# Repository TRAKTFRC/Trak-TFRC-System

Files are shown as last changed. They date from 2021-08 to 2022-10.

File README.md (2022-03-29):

# Trak-TFRC Product Feature Brief

## Primary goals

To develop and create low power and wireless open source technology that aids in large-scale and long-term wildlife research, conservation, and monitoring the health of ecosystems.
Device list:
1. Lora Base Station
2. TamaCollar
3. SmallCollar
4. MediumCollar
5. Mouse Motel
6. Tamarin Group Monitor  
Names subject to change  

### Device Feature List 

#### LoRa Base Station (AKA LoraTester1) 

A compact, portable device that can transmit and receive Lora messages, as well as store, display, and repeat them.  
- Durable IP66 enclosure with tamper-proof controls and secure mount points  
- LoRa 915Mhz/433Mhz with external SMA antenna mount  
- OLED display  
- SD card for data logging  
- RTC for accurate time keeping  
- GPS module  
- Rechargeable battery for operating in portable mode or when deployed in the field with solar power  
- Multiple modes of operation for receiving & logging LoRa messages, acting as a repeater, or transmitting data.  
- Optional features currently under consideration-  
    - USB connection to allow streaming of LoRa data in realtime to a PC  
    - Operating in a mesh network to extend the range of LoRa Message reception.  

Product usage & lifecycle notes- 
The LT1 units are primarily intended to be either used in handheld mode, or deployed as receivers  near feeding/monitoring sites to receive signals from collars. Ideally they should operate in a mesh to allow us to receive signals over a broader area in the dense amazonian jungle. 
As these are stationary devices mounted either to towers or tall vantage points, maintenance is much easier to perform and we hope these devices can last upwards of 5 years. 
The LT1 is a fairly flexible device, beyond changing it’s operating mode, users may wish to add additional sensors to monitor meteorological data or other.
 
#### TamaCollar

A lightweight tracker collar specifically designed to aid in tracking mature Tamarin species in the Peruvian Amazon.

- IP67 case/resin potting  
- Size- <30*25*6mm  
- Weight- <15g including ball chain collar  
- LoRa 915Mhz/433Mhz  
- RTC for accurate time keeping  
- GPS module  
- Primary non-rechargeable battery  
- User configurable transmission schedule  
- Optional features currently under consideration-  
    - Data logging in case of successful device retrieval

Product usage & lifecycle notes-  
The TC1 units are primarily designed to track wild Emperor Tamarins and Saddleback Tamarins, which are small new world monkeys weighing in at around 500g when grown.  
These lightweight disposable collars are shipped with a magnet taped near the internal reedswitch, and will activate when the vet who’s attaching the devices removes the magnet.   
In most cases, we will be programming the collars and shipping them sealed and ready-to-use, but configurable schedules are preferred. After a period of time, the crimp on the ball chain that holds the collar on will give way and fall off the animal. It is not expected to be recovered in most cases, but in the event that it is recovered, we can take apart the case and reuse the collars with minimal effort.  
Changes to make-  
- We are expecting to add a GPS antenna if required to help improve the GPS lock, both antennas would need to be as low-profile as possible. 
  
#### Tamarin Group Monitor

A deployable station to automate data collection from Tamarins and similar species
- Versatile and reconfigurable for different usecases
- Collects Weight, RFID readings, & images 
- flexible wake triggers
- Transmits data & trigger notifications over LoRa network.

#### SmallCollar

A minute tracker designed to aid in tracking smaller marsupials and rodents under 250g in the Peruvian Amazon.
At present, we are defining the brief for SC1 to allow us to monitor smaller animals than TC1, although no development has taken place yet. The goalposts are flexible so that we can push GPS monitoring to its absolute limits and bring the size and weight down as far as feasible. 
- IP67 case/resin potting  
- Size- TBD  
- Weight- <TBD including ball chain collar  
- LoRa 915Mhz/433Mhz  
- RTC for accurate time keeping  
- GPS module  
- Primary non-rechargeable battery  
- User configurable transmission schedule

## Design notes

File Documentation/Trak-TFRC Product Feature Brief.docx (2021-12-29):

# Trak-TFRC Product Feature Brief

# Primary goals

To develop and create low power and wireless open source technology that aids in large-scale and long-term wildlife research, conservation, and monitoring the health of ecosystems.

Device list:

1. Lora Base Station
2. TamaCollar
3. SmallCollar
4. MediumCollar
5. Mouse Motel
6. Tamarin Group Monitor

Names subject to change

# Device Feature List

## LoRa Base Station (AKA LoraTester1)

A compact, portable device that can transmit and receive Lora messages, as well as store, display, and repeat them.

- Durable IP66 enclosure with tamper-proof controls and secure mount points
- LoRa 915Mhz/433Mhz with external SMA antenna mount
- OLED display
- SD card for data logging
- RTC for accurate time keeping
- GPS module
- Rechargeable battery for operating in portable mode or when deployed in the field with solar power
- Multiple modes of operation for receiving & logging LoRa messages, acting as a repeater, or transmitting data.
- Optional features currently under consideration-
  - USB connection to allow streaming of LoRa data in realtime to a PC
  - Operating in a mesh network to extend the range of LoRa Message reception.

Product usage & lifecycle notes-

The LT1 units are primarily intended to be either used in handheld mode, or deployed as receivers near feeding/monitoring sites to receive signals from collars. Ideally they should operate in a mesh to allow us to receive signals over a broader area in the dense amazonian jungle.

As these are stationary devices mounted either to towers or tall vantage points, maintenance is much easier to perform and we hope these devices can last upwards of 5 years.

The LT1 is a fairly flexible device, beyond changing it’s operating mode, users may wish to add additional sensors to monitor meteorological data or other.

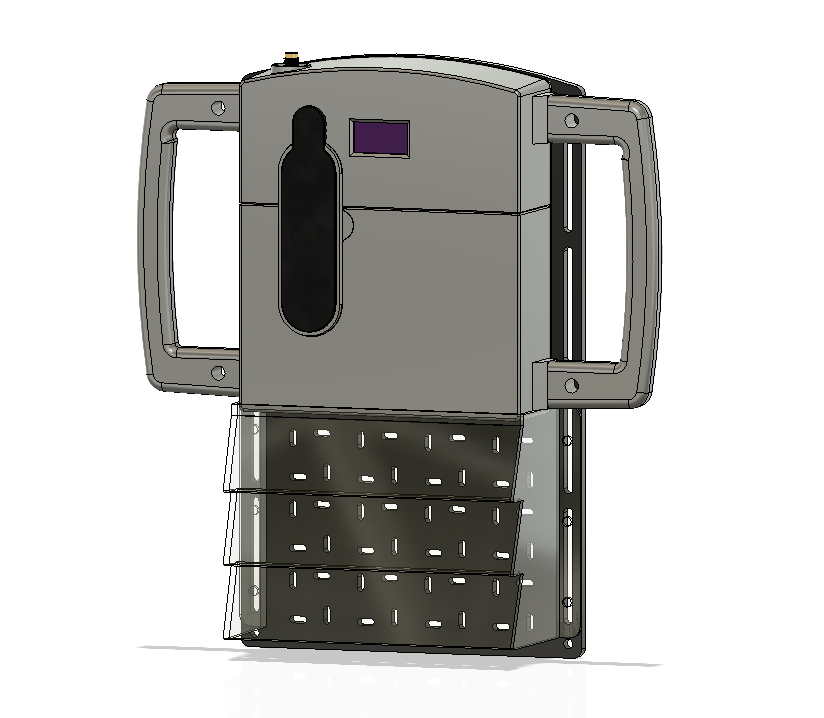
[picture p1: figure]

## TamaCollar

A lightweight tracker collar specifically designed to aid in tracking mature Tamarin species in the Peruvian Amazon.

- IP67 case/resin potting
- Size- <30X25X6mm
- Weight- <15g including ball chain collar
- LoRa 915Mhz/433Mhz
- RTC for accurate time keeping
- GPS module
- Primary non-rechargeable battery
- User configurable transmission schedule
- Optional features currently under consideration-
  - Data logging in case of successful device retrieval

Product usage & lifecycle notes-

The TC1 units are primarily designed to track wild Emperor Tamarins and Saddleback Tamarins, which are small new world monkeys weighing in at around 500g when grown.

These lightweight disposable collars are shipped with a magnet taped near the internal reedswitch, and will activate when the vet who’s attaching the devices removes the magnet.

In most cases, we will be programming the collars and shipping them sealed and ready-to-use, but configurable schedules are preferred. After a period of time, the crimp on the ball chain that holds the collar on will give way and fall off the animal. It is not expected to be recovered in most cases, but in the event that it is recovered, we can take apart the case and reuse the collars with minimal effort.

Changes to make-

- We are expecting to add a GPS antenna if required to help improve the GPS lock, both antennas would need to be as low-profile as possible.

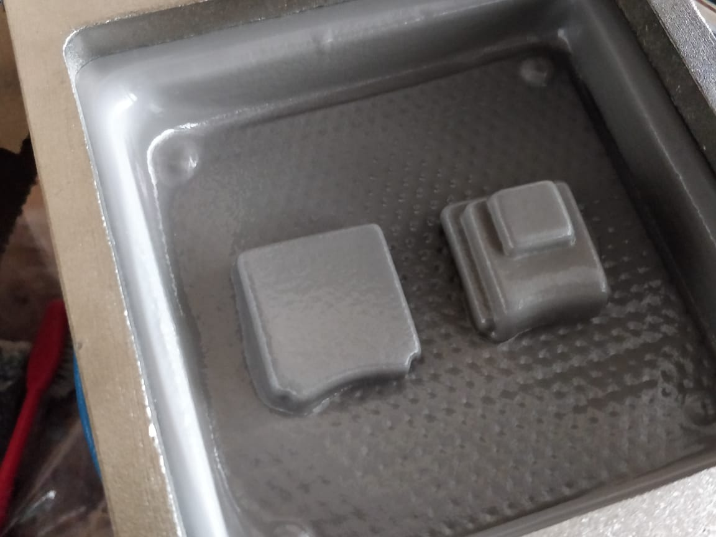
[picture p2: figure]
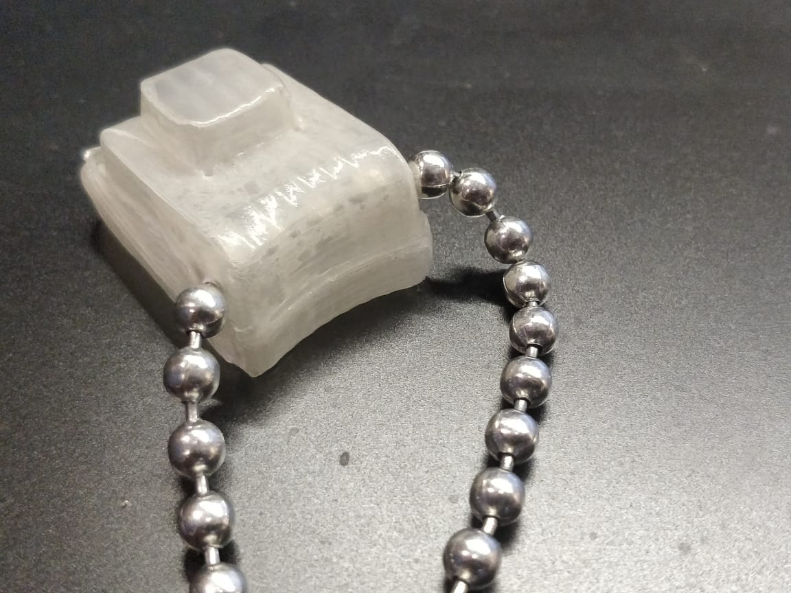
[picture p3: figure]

## SmallCollar

A minute tracker designed to aid in tracking smaller marsupials and rodents under 250g in the Peruvian Amazon.

At present, we are defining the brief for SC1 to allow us to monitor smaller animals than TC1, although no development has taken place yet. The goalposts are flexible so that we can push GPS monitoring to its absolute limits and bring the size and weight down as far as feasible.

- IP67 case/resin potting
- Size- TBD
- Weight- <TBD including ball chain collar
- LoRa 915Mhz/433Mhz
- RTC for accurate time keeping
- GPS module
- Primary non-rechargeable battery
- User configurable transmission schedule

## Tamarin Group Monitor-

A sample and data collection station to automate data collection from Tamarins and similar species.

- Autonomously collects data and transmits state via LoRa
- Stores and logs information to be manually retrieved via SD card
- Vital Data points-
  - Images
  - Weight
  - Subcutaneous RFID tag reading
  - Time
- Vital Sample points-
  - Hair/Fur
  - Faeces
  - Urine

Common points between TGM and Mouse Motel-

- Structure- Monitor unit
- Hardware- LoRa, Camera module, RTC, strain gauge IC, rechargeable & replaceable battery, power switch.
- Data- Camera, weighing scale (different size), Time
- Samples- Hair, Faeces, Urine

Differences-

- Structure- Enclosure size & door locations
- Hardware- RFID (TGM), Servo door activation (MM), night vision camera (MM)
- Data- Smaller strain gauge (MM)

# Timeline & Major Goals

- October End- Test and push TC1 and LT1 code to production
- November- Dispatch TC1 to Peru, TC1.1 as well if possible.
- March- Finalize and dispatch the following products to Peru
  - TamaCollar1.1
  - SmallCollar1
  - MediumCollar1.1
  - LoraTester1.1
  - TamaGroupMonitor/trap monitor
  - Mouse Motel

Note, I’ll make a high level gantt chart here

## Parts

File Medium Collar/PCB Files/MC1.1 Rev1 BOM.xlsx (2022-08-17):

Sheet: Basic Version
Basic Version |  |  |  |  |  |  | Note, The Embedded charging version requires componets D2 and R7 to be populated.
Qty | Value | Device | Package | Parts | Description | LINK
5 | 0.1uF | C_CHIP-0805(2012-METRIC) | CAPC2012X110 | C5, C6, C7, C8, C9 | Capacitor - Generic | https://www.sunrom.com/p/100nf-104-0805-2012-metric
2 | 1uF | C_CHIP-0805(2012-METRIC) | CAPC2012X110 | C3, C4 | Capacitor - Generic | https://www.sunrom.com/p/1uf-105-smd-0805-pack-of-10
2 | 33pF | C_CHIP-0805(2012-METRIC) | CAPC2012X110 | C1, C2 | Capacitor - Generic | https://www.evelta.com/33-pf-50v-0805-smd-multilayer-ceramic-capacitors-0805cg330j500nt-fenghua/
1 | 4.7uF | C_CHIP-0805(2012-METRIC) | CAPC2012X110 | C10 | Capacitor - Generic | https://www.evelta.com/4-7-uf-16v-0805-smd-multi-layer-ceramic-capacitor-0805x475k160ct-walsin/
4 | 10k | R_CHIP-0805(2012-METRIC) | RESC2012X65 | R3, R4, R5, R6 | Resistor Fixed - Generic | https://www.sunrom.com/p/10k-1-0805-pack-of-100
2 | 4.7k | R_CHIP-0805(2012-METRIC) | RESC2012X65 | R1, R2 | Resistor Fixed - Generic | https://www.sunrom.com/p/4k7-1-0805-pack-of-100
1 | 8mhz | CRYSTALHC49UP | HC49UP | Q1 | CRYSTAL | https://www.evelta.com/hc-49smd-8mhz-20pf-20ppm-2pad-smd-smt-quartz-crystal/
1 | ATMEGA328P-AU | ATMEGA328P-AU | QFP32_7X7_0.80 | U1 | 8-bit AVR Microcontroller | https://www.evelta.com/atmega328p-au-ic-mcu-8bit-32kb-flash-32tqfp/
1 | CR1220_SMD | CR1220_SMD | CR1220_2P_SMD | BATT2 |  | https://www.sunrom.com/p/battery-socket-for-cr1220
1 | DIODE | DIODEDO-214AC(SMA) | DIOM5226X290N | D1 | Diode Rectifier - Generic | https://www.sunrom.com/p/m7-1n4007-smd-1a-diode
1 | DS3231MZ+ | DS3231MZ+ | DS3231MZ+_SOIC8 | U5 |  | https://www.evelta.com/ds3231mz-maxim-integrated-alarm-rtc-i2c-2-3-v-to-5-5-v/
1 | 24LC128T-I/SN | 24LC128T-I/SN | SOIC8-N_MC_MCH | U6 |  | https://www.evelta.com/24lc512-i-sn-microchip-technology-eeprom-i2c-512-kbit/
1 | L80_GNSS_MODULE | L80_GNSS_MODULE | L80_PACKAGE | U3 | GPS module with an embedded patch antenna (15mmx15mmx4mm)
1 | LORA_RFM95W-915S2_MODULE | LORA_RFM95W-915S2_MODULE | LORA_RFM95W-915S2_16MODULE | U2 |  | https://www.digikey.in/product-detail/en/rf-solutions/RFM95W-915S2/RFM95W-915S2-ND/6564923
2 | PMOSFET | PMOSFET_SOT23 | SOT23 | M1, M2 | P-Channel MOSFET - Generic | https://www.sunrom.com/p/ao3401-a19t-sot-23-p-ch-mosfet
1 | REED_SWITCH | REED_SWITCH | REED_CT05 | SW1
1 | U.FL-R-SMT-101 | U.FL-R-SMT-101 | U.FL-R-SMT-1(XX) | ANT2 | U.FL (UMCC) Connector Receptacle, Male Pin 50Ohm Surface Mount Solder | https://www.sunrom.com/p/rf-antenna-connector-smd-ipx-ipex-ulf-mhf
2 | 470R | R_CHIP-0805(2012-METRIC) | RESC2012X65 | R8, R9 | Resistor Fixed - Generic | https://www.sunrom.com/p/470r-1-0805-pack-of-100
 | DO NOT POPULATE- D2, R7

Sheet: Embedded Batt Charging
Embedded Batt Charging Version |  |  |  |  |  |  | Note, The Embedded charging version requires componets D2 and R7 to be populated.
Qty | Value | Device | Package | Parts | Description | LINK
5 | 0.1uF | C_CHIP-0805(2012-METRIC) | CAPC2012X110 | C5, C6, C7, C8, C9 | Capacitor - Generic | https://www.sunrom.com/p/100nf-104-0805-2012-metric
2 | 1uF | C_CHIP-0805(2012-METRIC) | CAPC2012X110 | C3, C4 | Capacitor - Generic | https://www.sunrom.com/p/1uf-105-smd-0805-pack-of-10
2 | 33pF | C_CHIP-0805(2012-METRIC) | CAPC2012X110 | C1, C2 | Capacitor - Generic | https://www.evelta.com/33-pf-50v-0805-smd-multilayer-ceramic-capacitors-0805cg330j500nt-fenghua/
1 | 4.7uF | C_CHIP-0805(2012-METRIC) | CAPC2012X110 | C10 | Capacitor - Generic | https://www.evelta.com/4-7-uf-16v-0805-smd-multi-layer-ceramic-capacitor-0805x475k160ct-walsin/
4 | 10k | R_CHIP-0805(2012-METRIC) | RESC2012X65 | R3, R4, R5, R6 | Resistor Fixed - Generic | https://www.sunrom.com/p/10k-1-0805-pack-of-100
2 | 4.7k | R_CHIP-0805(2012-METRIC) | RESC2012X65 | R1, R2 | Resistor Fixed - Generic | https://www.sunrom.com/p/4k7-1-0805-pack-of-100
1 | 1k | R_CHIP-0805(2012-METRIC) | RESC2012X65 | R7 | Resistor Fixed - Generic | https://www.sunrom.com/p/1k-1-0805-pack-of-100
1 | 8mhz | CRYSTALHC49UP | HC49UP | Q1 | CRYSTAL | https://www.evelta.com/hc-49smd-8mhz-20pf-20ppm-2pad-smd-smt-quartz-crystal/
1 | ATMEGA328P-AU | ATMEGA328P-AU | QFP32_7X7_0.80 | U1 | 8-bit AVR Microcontroller | https://www.evelta.com/atmega328p-au-ic-mcu-8bit-32kb-flash-32tqfp/
1 | CR1220_SMD | CR1220_SMD | CR1220_2P_SMD | BATT2 |  | https://www.sunrom.com/p/battery-socket-for-cr1220
2 | DIODE | DIODEDO-214AC(SMA) | DIOM5226X290N | D1, D2 | Diode Rectifier - Generic | https://www.sunrom.com/p/m7-1n4007-smd-1a-diode
1 | DS3231MZ+ | DS3231MZ+ | DS3231MZ+_SOIC8 | U5 |  | https://www.evelta.com/ds3231mz-maxim-integrated-alarm-rtc-i2c-2-3-v-to-5-5-v/
1 | 24LC128T-I/SN | 24LC128T-I/SN | SOIC8-N_MC_MCH | U6 |  | https://www.evelta.com/24lc512-i-sn-microchip-technology-eeprom-i2c-512-kbit/
1 | L80_GNSS_MODULE | L80_GNSS_MODULE | L80_PACKAGE | U3 | GPS module with an embedded patch antenna (15mmx15mmx4mm)
1 | LORA_RFM95W-915S2_MODULE | LORA_RFM95W-915S2_MODULE | LORA_RFM95W-915S2_16MODULE | U2 |  | https://www.digikey.in/product-detail/en/rf-solutions/RFM95W-915S2/RFM95W-915S2-ND/6564923
2 | PMOSFET | PMOSFET_SOT23 | SOT23 | M1, M2 | P-Channel MOSFET - Generic | https://www.sunrom.com/p/ao3401-a19t-sot-23-p-ch-mosfet
1 | REED_SWITCH | REED_SWITCH | REED_CT05 | SW1
1 | U.FL-R-SMT-101 | U.FL-R-SMT-101 | U.FL-R-SMT-1(XX) | ANT2 | U.FL (UMCC) Connector Receptacle, Male Pin 50Ohm Surface Mount Solder | https://www.sunrom.com/p/rf-antenna-connector-smd-ipx-ipex-ulf-mhf
2 | 470R | R_CHIP-0805(2012-METRIC) | RESC2012X65 | R8, R9 | Resistor Fixed - Generic | https://www.sunrom.com/p/470r-1-0805-pack-of-100

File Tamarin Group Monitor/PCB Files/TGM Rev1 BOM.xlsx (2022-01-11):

Initial Run Units- | 10 | Note, some components like caps will need larger order quantities |  |  |  |  | ECAD Version- v21 TGM Rev1
Order Quantity | Qty | Value | Package | Parts | Description | CATEGORY | LINK
10 | 1 | CR2032 | BATTERY-20MM_PTH | BACKUP_BATT1 | Battery - Single Cell |  | https://www.evelta.com/3v-litium-battery-holder/
10 | 1 | Schottky Diode | SCHOTTKY_DO-219 | D1 | Schottky Diode - Popular parts |  | https://www.sunrom.com/p/1n5819-b5819w-1n5819w-s4-sod123-1206-1a-40v-schottky-diode
60 | 6 | 0.1uF | C_CHIP-0805(2012-METRIC) | C5, C6, C7, C8, C9, C16 | Capacitor - Generic |  | https://www.sunrom.com/p/100nf-104-0805-2012-metric
10 | 1 | 100uF | C-POL | C4 | Capacitor Polarised - Generic |  | https://www.evelta.com/100uf-25v-electrolytic-capacitor/
60 | 6 | 10k | R_CHIP-0805(2012-METRIC) | R4, R5, R6, R7, R8, R9 | Resistor Fixed - Generic |  | https://www.sunrom.com/p/10k-1-0805-pack-of-100
20 | 2 | 10uF | C_CHIP-0805(2012-METRIC) | C3, C12 | Capacitor - Generic |  | https://www.sunrom.com/p/10uf-106-smd-0805-pack-of-10
10 | 1 | 1P2T_SLIDE_SWITCHRIGHT | 1P2T_SLIDE_SWITCHRIGHT | S1 |  |  | https://www.sunrom.com/p/slide-switch-1p2t-high-current-right-angle
30 | 3 | 1uF | C_CHIP-0805(2012-METRIC) | C11, C13, C15 | Capacitor - Generic |  | https://www.sunrom.com/p/1uf-105-smd-0805-pack-of-10
40 | 4 | 2828XX-4282837-4 | 2828XX-4282837-4 | T1, T2, T3, T4 | 4 Position Wire to Board Terminal Block Horizontal with Board |  | https://robu.in/product/4-pin-5-08mm-pitch-pluggable-screw-terminal-block-pack-of-3/
20 | 2 | 33pF | C_CHIP-0805(2012-METRIC) | C1, C2 | Capacitor - Generic |  | https://www.evelta.com/33-pf-50v-0805-smd-multilayer-ceramic-capacitors-0805cg330j500nt-fenghua/
10 | 1 | 4-pin JST XH | B4B-XH-A | JP_RFID | XH Connector Top Entry - 4POS |  | Remark- We can either solder wires directly, or use two JST XH 4-pin connectors and a female-female cable.
20 | 2 | 4.7k | R_CHIP-0805(2012-METRIC) | R1, R2 | Resistor Fixed - Generic |  | https://www.sunrom.com/p/4k7-1-0805-pack-of-100
10 | 1 | 4.7uF | C_CHIP-0805(2012-METRIC) | C10 | Capacitor - Generic |  | https://www.evelta.com/4-7-uf-16v-0805-smd-multi-layer-ceramic-capacitor-0805x475k160ct-walsin/
10 | 1 | 470R | R_CHIP-0805(2012-METRIC) | R3 | Resistor Fixed - Generic |  | https://www.sunrom.com/p/470r-1-0805-pack-of-100
10 | 1 | 470uF | C-POLCAP_5P_5X11 | C14 | Capacitor Polarised - Generic |  | https://www.evelta.com/470uf-25v-electrolytic-capacitor/
10 | 1 | 4MHz | CRYSTALHC49UP | Q1 | CRYSTAL |  | https://www.evelta.com/hc-49smd-4mhz-20pf-20ppm-2pad-smd-smt-quartz-crystal/
10 | 1 | 68uh | INDUCTOR_12MM_SHIELDED | L1 |  |  | https://www.sunrom.com/p/68uh-680-12mm-inductor
10 | 1 | ATMEGA328P-AU | ATMEGA328P-AU | U1 | 8-bit AVR Microcontroller |  | https://www.evelta.com/atmega328p-au-ic-mcu-8bit-32kb-flash-32tqfp/
10 | 1 | DS3231MZ+ | DS3231MZ+ | U5 |  |  | https://www.evelta.com/ds3231mz-maxim-integrated-alarm-rtc-i2c-2-3-v-to-5-5-v/
10 | 1 | ESP32-CAM | ESP32-CAM | U6
20 | 2 | HX711 Load cell amp Breakout | HX711_BREAKOUT | U3, U4
10 | 1 | LDO-LM11173.3MP | LDO-LM11173.3MP | P2 | 800mA Low-Dropout Linear Regulator |  | https://www.sunrom.com/m/4004
10 | 1 | LED_BLUE | LED_RADIAL_BLUE | D2 | LED - Generic |  | https://www.sunrom.com/p/blue-led-3mm
10 | 1 | LORA_RFM95W-915S2_MODULE | LORA_RFM95W-915S2_MODULE | U2 |  |  | https://www.digikey.in/product-detail/en/rf-solutions/RFM95W-915S2/RFM95W-915S2-ND/6564923
20 | 2 | MOMENTARY-SWITCH-SPST-PTH-12MM | MOMENTARY-SWITCH-SPST-PTH-12MM | S2, S3 | Momentary Switch (Pushbutton) - SPST |  | https://www.sunrom.com/p/tactile-switch-square-head-omron-b3f-4055-12x12x73mm
20 | 2 | NMOSFET | NMOSFETSOT23 | M2, M3 | N-Channel MOSFET - Generic |  | https://www.evelta.com/bss138lt1g-50v-220ma-n-channel-transistor-surface-mount-sot-23-3/
10 | 1 | PMOSFET | PMOSFET_SOT23 | M1 | P-Channel MOSFET - Generic |  | https://www.sunrom.com/p/ao3401-a19t-sot-23-p-ch-mosfet
10 | 1 | XL1509 | XL1509 | P1 |  |  | https://www.sunrom.com/m/6161
10 | 1 | SMA Connector | SMACONNECTOR_EDGE | SMA | SMA Connector
10 | 1 | Battery Holder |  |  |  |  | https://robu.in/product/12v-8-x-aa-battery-clip-slot-holder-stack-box-case/
 |  | SMA-KE connectors
10 | 1 | https://inkocean.in/products/1-6-partial-foot-extension-sma-sma-ke-radio-base-screw-hole-in-the-outer-tooth-profile-coaxial-connector-11mm |  |  |  |  | Remark- both these connectors are seemingly identical, hence I've included both links to be ordered at your discretion.
10 | 1 | https://inkocean.in/products/longer-sma-ke-outer-screw-hole-declination-rf-antenna-pedestal-base-sma-connector-sma-female-connector-nest
 |  | Additional Accessories | Required for the case
20 | 2 | Roundshell 16mm pair |  |  |  |  | https://www.sunrom.com/p/8p-metal-mini-round-shell-aviation-male-and-female-circular-connectors-gx16-16mm
20 | 2 | Cable Glands for the Load cells |  |  |  |  | https://www.sunrom.com/p/pg7-white-nylon-cable-gland-for-cable-dia-3-6mm
20 | 2 | Cable Glands for RFID wires |  |  |  |  | https://www.sunrom.com/p/pg11-white-nylon-cable-gland-for-cable-dia-7-9mm
10 | 1 | Slide switch |  |  | The device should use the right angle connectors,but in case they don't fit these are for backup. |  | https://www.sunrom.com/p/slide-switch-1p2t-high-current-straight
10 | 1 | https://www.sunrom.com/p/sma-hex-nut-and-washer-set
20 | 2 | https://www.sunrom.com/p/black-round-cap-for-omron-b3f-series-switches
10 | 1 | https://www.sunrom.com/p/dust-cover-for-gx16-16mm-aviation-plug-connector-waterproof-rubber-cap
10 | 1 | https://www.sunrom.com/p/4p-metal-mini-round-shell-aviation-male-and-female-circular-connectors-gx16-16mm
 |  | Non-populated components
20 | 2 | PINHD-1X2 | PINHD-1X2 | JP3P, JP4 | PIN HEADER
10 | 1 | PINHD-1X3 | PINHD-1X3 | JP_PIR | PIN HEADER
20 | 2 | PINHD-1X8 | PINHD-1X8 | JP3, JP5 | PIN HEADER
80 | 8 | MOUNTING_HOLES | MOUNTING_HOLES | H1, H2, H3, H4, H5, H6, H7, H8
20 | 2 | MOUNTING_HOLESPLAIN | MOUNTING_HOLESPLAIN | H9, H10
60 | 6 | FIDUCIAL | FIDUCIAL | F1, F2, F3, F4, F5, F6 | For use by pick and place machines to calibrate the vision/machine, 1mm
10 | 1 | FTDI_DEVICE | FTDI_DEVICE | JP1 | Connector which mates to FTDI basic or FTDI cable.
10 | 1 |  | RESISTOR_JUMPER | D2R
10 | 1 | 2828XX-2282837-2 | 2828XX-2282837-2 | PWR | 2 Position Wire to Board Terminal Block Horizontal with Board
10 | 1 | AVR_SPI_PRG_6PTH | AVR_SPI_PRG_6PTH | JP2 | AVR ISP 6 Pin
90 | 9 | BREAKOUT_PADL | BREAKOUT_PADL | ADC7, H1A+, H1A-, H1B+, H1B-, H2A+, H2A-, H2B+, H2B-
20 | 2 | NO_JUMPER | NO_JUMPER | J1, J2

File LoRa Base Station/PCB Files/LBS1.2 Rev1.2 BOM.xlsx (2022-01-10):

Initial Run Units- | 10 | Note, some components like caps will need larger order quantities |  |  |  |  | ECAD Version- v26
Order Quantity | Qty | Value | Package | Parts | Description | CATEGORY | LINK
10 | 1 | CR2032 Holder | BATTCOM_20MM_PTH | BACKUP_BATT1 | Battery - Single Cell |  | https://www.evelta.com/3v-litium-battery-holder/
10 | 1 | SMA Edge-mount Connector Long | SMA_EDGELAUNCH | SMA | SMA Connector
50 | 5 | 0.1uF | CAPC2012X110 | C3, C4, C5, C7, C15 | Capacitor - Generic | Capacitor | https://www.sunrom.com/p/100nf-104-smd-0805-pack-of-20
10 | 1 | 0.96_OLED_I2C | OLED_0.96_I2C | OLED1 |  |  | https://www.module143.com/0.96inch-i2c-oled-module
10 | 1 | 100uF | CAP_2P_5X11 | C10 | Capacitor Polarised - Generic |  | https://www.evelta.com/100uf-25v-electrolytic-capacitor/
70 | 7 | 10k | RESC2012X65 | R3, R4, R5, R6, R11, R13, R14 | Resistor Fixed - Generic | Resistor | https://www.sunrom.com/p/10k-1-0805-pack-of-100
20 | 2 | 10uF | CAPC2012X110 | C8, C9 | Capacitor - Generic | Capacitor | https://www.sunrom.com/p/10uf-106-smd-0805-pack-of-10
10 | 1 | 10uF | C_TANTALUM-1206(3216-METRIC) | C6 | Capacitor - Generic | Capacitor | https://www.sunrom.com/p/10uf-25v-tantalum
10 | 1 | 1N5820 | SODFL3718X115 | D1 | Schottky Diode - Popular parts |  | https://www.sunrom.com/p/1n5819-b5819w-1n5819w-s4-sod123-1206-1a-40v-schottky-diode
10 | 1 | 1P2T_SLIDE_SWITCH | 1P2T_SLIDE_SWITCH | S1 |  |  | https://www.sunrom.com/p/slide-switch-1p2t-high-current-straight
30 | 3 | 1uF | CAPC2012X110 | C11, C12, C13 | Capacitor - Generic | Capacitor | https://www.sunrom.com/p/1uf-105-smd-0805-pack-of-10
20 | 2 | 4.7k | RESC2012X65 | R1, R2 | Resistor Fixed - Generic | Resistor | https://www.sunrom.com/p/4k7-1-0805-pack-of-100
10 | 1 | 5.1M | R_CHIP-0805(2012-METRIC) | R12 | Resistor Fixed - Generic | Resistor | https://www.sunrom.com/p/5m1-1-0805
40 | 4 | 5.1k | R_CHIP-0805(2012-METRIC) | R7, R8, R9, R10 | Resistor Fixed - Generic | Resistor | https://www.evelta.com/5k1-5-0805-smd-resistor-royal-ohm-0805W8J0512T5E/
10 | 1 | 470R | R_CHIP-0805(2012-METRIC) | R15 | Resistor Fixed - Generic |  | https://www.sunrom.com/p/470r-1-0805-pack-of-100
10 | 1 | 470uF | CAP_5P_10X12.5 | C14 | Capacitor Polarised - Generic |  | https://www.evelta.com/470uf-25v-electrolytic-capacitor/
10 | 1 | 68uh | INDUCTOR_12X12MM | L1 |  |  | https://www.sunrom.com/p/68uh-680-12mm-inductor
10 | 1 | ESP32-WROOM-32E | ESP32-WROOM-32E | U1
10 | 1 | 32.768khz | YT-38(RTC_CRYSTAL) | Q1 | Thru-Hole Tuning Fork | Crystals | https://www.sunrom.com/p/32768-khz-rtc-crystal-t38
20 | 2 | MMBT2222AL | SOT95P237X112 | Q2, Q3 | NPN - Popular parts | N-Channel MOSFET - Generic | https://www.evelta.com/mmbt2222alt1g-40v-600ma-npn-bipolar-silicon-transistor-3-pin-sot-23/
10 | 1 | PMOSFET | PMOSFET_SOT23 | U3 |  | P-Channel MOSFET - Generic | https://www.sunrom.com/p/ao3401-a19t-sot-23-p-ch-mosfet
10 | 1 | LDO-LM11173.3MP | SOT223 | P2 | 800mA Low-Dropout Linear Regulator |  | https://www.sunrom.com/m/4004
10 | 1 | LORA_RFM95W-915S2_MODULE | LORA_RFM95W-915S2_16MODULE | U4 |  |  | https://www.digikey.in/product-detail/en/rf-solutions/RFM95W-915S2/RFM95W-915S2-ND/6564923
20 | 2 | MOMENTARY-SWITCH-SPST-PTH-12MM | TACTILE_SWITCH_PTH_12MM | S2, S3 | Momentary Switch (Pushbutton) - SPST |  | https://www.sunrom.com/p/tactile-switch-square-head-omron-b3f-4055-12x12x73mm
20 | 2 | MOMENTARY-SWITCH-SPST-PTH-6MM |  | EN, BOOT | Momentary Switch (Pushbutton) - SPST |  | https://www.sunrom.com/p/tactile-switch-6x6x43mm
10 | 1 | L80_GNSS_MODULE | L80_PACKAGE | U2 | GPS module with an embedded patch antenna (15mmx15mmx4mm) |  | https://www.rhydolabz.com/wireless-gps-c-130_186/gps-smd-module-with-antennapa6h-p-1911.html
10 | 1 | SD_MICRO_SOCKET-204270SD_FULL | SD_CARD_SOCKET-794212 | SD |  |  | https://www.sunrom.com/p/full-sd-card-socket
20 | 2 | TERMINAL_BLOCK | TERMBLK_508-2N | JP4A, JP5A, JP6 |  |  | https://www.sunrom.com/p/2p-5mm-10a-screw-terminal-light
10 | 1 | XL1509 | XL1509_SOIC8 | P1 |  |  | https://www.sunrom.com/m/6161
20 | 2 | USB-C_POWER_SUN5463 | USB-C_POWER_SUN5463 | USB1, USB2 |  |  | https://www.sunrom.com/p/usb-type-c-female-6pin-for-powercharging-reversible
 |  | Optional components, Do not populate
10 | 1 | DS3231MZ+ | DS3231MZ+_SOIC8 | U5 |  |  | https://www.evelta.com/ds3231mz-maxim-integrated-alarm-rtc-i2c-2-3-v-to-5-5-v/
20 | 2 | 15pF | C_CHIP-0805(2012-METRIC) | C1, C2 | Capacitor - Generic |  | Capacitor | https://www.sunrom.com/p/15pf-150-0805-2012-metric
 |  | SMA-KE connectors
10 | 1 | https://inkocean.in/products/1-6-partial-foot-extension-sma-sma-ke-radio-base-screw-hole-in-the-outer-tooth-profile-coaxial-connector-11mm |  |  |  |  | Remark- both these connectors are seemingly identical, hence I've included both links to be ordered at your discretion.
10 | 1 | https://inkocean.in/products/longer-sma-ke-outer-screw-hole-declination-rf-antenna-pedestal-base-sma-connector-sma-female-connector-nest
 |  | Additional Accessories
10 | 1 | https://www.sunrom.com/p/sma-hex-nut-and-washer-set |  |  |  |  | Remark- These following components will be required when we're assembling the device, but aren't strictly on the PCB.
20 | 2 | https://www.sunrom.com/p/black-round-cap-for-omron-b3f-series-switches
10 | 1 | https://www.sunrom.com/p/dust-cover-for-gx16-16mm-aviation-plug-connector-waterproof-rubber-cap
10 | 1 | https://www.sunrom.com/p/4p-metal-mini-round-shell-aviation-male-and-female-circular-connectors-gx16-16mm

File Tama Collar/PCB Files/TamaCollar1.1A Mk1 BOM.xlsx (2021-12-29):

Board Qty- | 10
Ordering Quantity | Qty | Value | Device | Package | Parts | Description | LINK
70 | 7 | 0.1uF | C_CHIP-0402(1005-METRIC) | CAPC1005X60 | C3, C4, C5, C6, C7, C9, C10 | Capacitor - Generic | https://www.evelta.com/100-nf-25v-0402-smd-multi-layer-ceramic-capacitor-0402x104k250ct-walsin/
20 | 2 | 4.7k | R_CHIP-0402(1005-METRIC) | RESC1005X40 | R1, R2 | Resistor Fixed - Generic | https://www.evelta.com/4-7k-1-0402-smd-thick-film-chip-resistor-royal-ohm-0402wgf4701tce/
70 | 7 | 10k | R_CHIP-0402(1005-METRIC) | RESC1005X40 | R3, R4, R5, R6, R7, R8, R10 | Resistor Fixed - Generic | https://www.evelta.com/10k-1-0402-smd-thick-film-chip-resistor-royal-ohm-0402wgf1002tce/
20 | 2 | 10pF | C_CHIP-0402(1005-METRIC) | CAPC1005X60 | C1, C2 | Capacitor - Generic | https://www.evelta.com/10-pf-50v-0402-smd-multilayer-ceramic-capacitors-cc0402jrnpo9bn100-yageo/
10 | 1 | 2.2uF | C_CHIP-0402(1005-METRIC) | CAPC1005X60 | C8 | Capacitor - Generic | Out of stock, will need to order from SP road.
10 | 1 | 22k | R_CHIP-0402(1005-METRIC) | RESC1005X40 | R9 | Resistor Fixed - Generic | https://www.evelta.com/22k-1-0402-smd-thick-film-chip-resistor-royal-ohm-0402wgf2202tce/
10 | 1 | 8mhz | CRYSTAL | CRYSTAL_NX3225GD | Q1 | CRYSTAL | https://www.evelta.com/nx3225gd-8mhz-std-cra-3-8mhz-50ppm-crystal-8pf-surface-mount-2-smd-for-automotive/
10 | 1 | ATMEGA328P-MU | ATMEGA328P-MU | QFN32_5X5_0.50 | U1 | 8-bit AVR Microcontroller | https://www.rhydolabz.com/components-microcontrollers-c-172_192/atmega328pmu-smd-p-2612.html
10 | 1 | DS3231MZ+ | DS3231MZ+ | DS3231MZ+_SOIC8 | U4 |  | https://www.evelta.com/ds3231mz-maxim-integrated-alarm-rtc-i2c-2-3-v-to-5-5-v/
10 | 1 | GPS_ORG1411 | GPS_ORG1411 | ORG1411 | U3
10 | 1 | TPS7A0318DBVR |  | MIC5205/TPS7A0318DBVR | P1 |  | https://www.evelta.com/mic5205ym5-adjustable-ldo-voltage-regulator-2-5-16v-input-165mvdrop-150maout/
10 | 1 | LORA_RFM95W-915S2_MODULETHT | LORA_RFM95W-915S2_MODULETHT | LORA_RFM95W-915S2_16STANDOFFMODULE | U2 |  | https://www.digikey.in/product-detail/en/rf-solutions/RFM95W-915S2/RFM95W-915S2-ND/6564923
10 | 1 | NMOSFET | NMOSFETSOT23 | SOT23 | Q2 | N-Channel MOSFET - Generic | https://www.evelta.com/bss138lt1g-50v-220ma-n-channel-transistor-surface-mount-sot-23-3/
10 | 1 | REED_SWITCH | REED_SWITCH | REED_CT05 | SW1
10 | 1 | RESONATOR_4MHZ | RESONATOR_4MHZ | RESONATOR_4MHZ | Q1

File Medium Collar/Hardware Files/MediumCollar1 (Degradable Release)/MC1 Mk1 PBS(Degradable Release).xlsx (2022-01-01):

MediumCollar1 (Degradable Release) - Product Breakdown Sheet |  |  |  |  |  |  |  |  |  | Pricing |  |  | Legend and Information
Part No. | Part Name | Material | Material Spec | Fabrication Process | Source | Qty. per Unit | Order Qty. | Stage | Remarks | Price Per Unit | Price per Product | Order Price | Part No. (#01-123) | MC1A10-001 = Main Model Number + Part Number Combined
MC1A00-000 | MediumCollar1 Mk1 |  |  |  |  | 1 | 40 | CAD Completed |  |  | ₹968 | ₹0 |  | MC1A10-001 = Batch Number
MC1A01-000 | Collar unit |  |  |  |  |  |  | CAD Completed |  |  |  |  |  | MC1A10-001 = Subassembly
MC1A01-001 | Type C Case | PETG |  | FDM 3D Printing |  | 1 |  | CAD Completed | Type C is for the ballchain/wire inside a 7mm rubber tube | ₹360 | ₹360 |  |  | MC1A10-001 = Part Number
MC1A01-002 | Type C Lid | PETG |  |  |  | 1 |  | CAD Completed |  | ₹80 | ₹80 |  | Part Name | A name or identifier (eg- Driving Camshaft)
MC1A01-003 | MC1 PCB | PETG |  |  |  | 1 |  | CAD Completed |  |  | ₹0 |  | Material
MC1A01-004 | LS14500 | Sourced | LS14500 (tab termination) |  | SAFT (through Manoj) | 1 |  | Sourced |  | 475 | ₹475 |  | Material Spec | material specifications, such as thickness or dimensions
MC1A01-005 | Plastite Screws CSK | Sourced | B4B6703010 |  | JC Gupta & Sons | 5 |  | Sourced |  | 5.6 | ₹28 |  | Process | Manufacturing Process (milling, routing, etc.)
MC1A01-006 | Magnet | Sourced |  |  |  | 1 |  | Sourced | Magnet to be taped opposite the open end of the MC1 case, to keep the device deactivated until in use. |  | ₹0 |  | Source | Specific manufacturer or Store to procure part from
MC1A01-012 | Steel wire rope | Sourced | 2mm 7*7 cable |  |  | 1 |  | Sourced |  | 9 | ₹9 |  | Required Quantity | Quantity Required to build 1 unit
MC1A01-013 | Collar tubing | Sourced | Rubber tube 2mm ID 4-8mm OD |  |  | 1 |  | Sourced |  |  | ₹0 |  | Order Quantity | Total Quantity required including spares
 |  |  |  |  |  |  |  |  |  |  |  |  | Status | Denotes current state of part/s
 |  |  |  |  |  |  |  |  |  |  |  |  | Remarks | Additional notes or remarks
 |  |  |  |  |  |  |  |  |  |  |  |  | Stages of Completion | Unstarted
 |  |  |  |  |  |  |  |  |  |  |  |  |  | In CAD
 |  |  |  |  |  |  |  |  |  |  |  |  |  | CAD Completed
 |  |  |  |  |  |  |  |  |  |  |  |  |  | Prototyping
 |  |  |  |  |  |  |  |  |  |  |  |  |  | Manufacturing
 | Expendables- |  |  |  |  |  |  |  |  |  |  |  |  | To Be Sourced
MC1A01-020 | Loctite SI 596 | Sourced |  | Sourced Locally | Zenith Chemicals or https://www.tryloctite.in/estore/gasketing-compounds-loctite-si-596-AD.GA.333670/ | 0.05 |  | Sourced |  | ₹320 | ₹16 |  |  | Sourced
 |  |  |  |  |  |  |  |  |  |  |  |  |  | Needs Assembly
 |  |  |  |  |  |  |  |  |  |  |  |  |  | Assembled
 | Extras-
 |  |  |  |  |  |  |  |  |  |  |  |  | Materials | Stainless Steel Sheet
 |  |  |  |  |  |  |  |  |  |  |  |  |  | Baltic Birch Ply
 |  |  |  |  |  |  |  |  |  |  |  |  |  | Sourced
 |  |  |  |  |  |  |  |  |  |  |  |  |  | EPDM
 |  |  |  |  |  |  |  |  |  |  |  |  |  | Acrylic
 |  |  |  |  |  |  |  |  |  |  |  |  |  | PETG
 |  |  |  |  |  |  |  |  |  |  |  |  |  | Resin
 |  |  |  |  |  |  |  |  |  |  |  |  |  | PCB
 |  |  |  |  |  |  |  |  |  |  |  |  |  | EVA
 |  |  |  |  |  |  |  |  |  |  |  |  | Fabrication Process | Sourced Locally
 |  |  |  |  |  |  |  |  |  |  |  |  |  | Sourced Internationally
 |  |  |  |  |  |  |  |  |  |  |  |  |  | Lasercut
 |  |  |  |  |  |  |  |  |  |  |  |  |  | Waterjet/manual
 |  |  |  |  |  |  |  |  |  |  |  |  |  | Fabrication (In-House)
 |  |  |  |  |  |  |  |  |  |  |  |  |  | FDM 3D Printing
 |  |  |  |  |  |  |  |  |  |  |  |  |  | Vacuum Cast
 |  |  |  |  |  |  |  |  |  |  |  |  |  | Vacuum Formed

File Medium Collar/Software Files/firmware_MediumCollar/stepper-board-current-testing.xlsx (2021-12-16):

Axis | Wave length | Step | Current
X | 700 | half | 1.57
Y | 700 | Sixteenth | 2.93
X | 500 | half | 1.12
Y | 500 | Sixteenth | 2.38
X | 300 | half | 0.57
Y | 300 | Sixteenth | 1.26

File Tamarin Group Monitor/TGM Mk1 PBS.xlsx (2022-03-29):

Tamarin Group Monitor 1 - Product Breakdown Sheet |  |  |  |  |  |  |  |  | Pricing |  |  | Legend and Information
Part No. | Part Name | Material | Material Spec | Fabrication Process | Source | Qty. per Unit | Order Qty. | Remarks | Price Per Unit | Price per Product | Order Price | Part No. (#01-123) | LT1A10-001 = Main Model Number + Part Number Combined
TGM1A00-000 | Tamarin Group Monitor Mk1 Rev1 |  |  |  |  | 1 | 40 |  |  | ₹129.9 | ₹0 |  | LT1A10-001 = Batch Number
TGM1A01-000 | MCU Unit |  |  |  |  | 1 |  |  |  |  |  |  | LT1A10-001 = Subassembly
TGM1A01-001 | Case | PETG |  | FDM 3D Printing |  | 1 |  |  |  |  |  |  | LT1A10-001 = Part Number
TGM1A01-002 | Case Button Plate | PETG |  | FDM 3D Printing |  | 1 |  |  |  |  |  | Part Name | A name or identifier (eg- Driving Camshaft)
TGM1A01-003 | Case Cover | PETG |  | FDM 3D Printing |  | 1 |  |  |  |  |  | Material
TGM1A01-004 | General Clamp | PETG |  | FDM 3D Printing |  | 3 |  | Used for mounting the MCU and Covers |  |  |  | Material Spec | material specifications, such as thickness or dimensions
TGM1A01-005 | Case Gasket | EPDM | 1mm | Waterjet/manual | Sanaa Rubber Products | 1 |  |  |  |  |  | Process | Manufacturing Process (milling, routing, etc.)
TGM1A01-006 | Acrylic LED/CAM Cover | Acrylic | 2mm (actual 1.8mm) | Lasercut |  | 1 |  | Same Acrylic cover used in Cam unit for camera cover |  |  |  | Source | Specific manufacturer or Store to procure part from
TGM1A01-007 | MCU PCB | Sourced |  | Sourced Locally |  | 1 |  | The MCU half of the TGM PCB |  |  |  | Required Quantity | Quantity Required to build 1 unit
TGM1A01-008 | Priority1 RFID Module | Sourced | RFIDRW-E-TTL | Sourced Internationally |  | 1 |  |  |  |  |  | Order Quantity | Total Quantity required including spares
TGM1A01-009 | JST Connector | Sourced | JST XH 2.5mm | Sourced Locally | https://www.sunrom.com/p/4-pin-jst-xh-25mm-both-side-female-10cm | 0.5 |  | Buy one connector and cut it in half, and solder leads directly to RFID PCB |  |  |  | Status | Denotes current state of part/s
TGM1A01-010 | Cable Gland PG7 | Sourced |  | Sourced Locally |  | 2 |  | Qty is 2-4 depending on configuration |  |  |  | Remarks | Additional notes or remarks
TGM1A01-011 | Cable Gland PG11 | Sourced |  | Sourced Locally |  | 2
LT1A01-009 | Button Caps | Sourced |  | Sourced Locally | Sunrom | 2 |  |  |  |  |  | Stages of Completion | Unstarted
LT1A01-010 | Button Cover | Acrylic | 5mm (actual 4.8mm) | Lasercut | Sunrom | 1 |  |  |  |  |  |  | In CAD
LT1A01-011 | Button Seal | EPDM | 1mm | Waterjet/manual |  | 1 |  |  |  |  |  |  | CAD Completed
LT1A01-014 | Round Shell Connector 16mm | Sourced | 8 ways | Sourced Locally | Sunrom | 1 |  |  |  |  |  |  | Prototyping
LT1A01-016 | PCB Mounting Bolts | Sourced | M3x6 MS | Sourced Locally |  | 5 |  |  |  |  |  |  | Manufacturing
LT1A01-017 | Case Closure Bolts | Sourced | M4x14 SS | Sourced Locally |  | 9 |  |  | ₹6.6 |  |  |  | To Be Sourced
LT1A01-018 | Case Closure Inserts | Sourced | M4x4 Brass | Sourced Locally |  | 9 |  |  | ₹1.5 |  |  |  | Sourced
LT1A01-020 | Fastener Rubber Washer | Sourced | 4mm ID, 8mm OD, 1mm CS | Sourced Locally |  | 9 |  | Buy 1.2x required, some have issues with poor moulding. |  |  |  |  | Needs Assembly
 |  |  |  |  |  |  |  |  |  |  |  |  | Assembled
TGM1A02-000 | Camera Unit |  |  |  |  |  |  |  |  |  |  | Materials | Stainless Steel Sheet
TGM1A02-001 | Cam Case | PETG |  | FDM 3D Printing |  | 1 |  |  |  |  |  |  | Baltic Birch Ply
TGM1A02-002 | Cam Cap | PETG |  | FDM 3D Printing |  | 1 |  |  |  |  |  |  | Sourced
TGM1A02-003 | PIR Cap | PETG |  | FDM 3D Printing |  | 1 |  |  |  |  |  |  | EPDM
TGM1A02-004 | PIR Clamp | PETG |  | FDM 3D Printing |  | 1 |  |  |  |  |  |  | Acrylic
TGM1A02-005 | Case Cover | PETG |  | FDM 3D Printing |  | 1 |  |  |  |  |  |  | PETG
TGM1A02-006 | Lid Clamp | PETG |  | FDM 3D Printing |  | 1 |  |  |  |  |  |  | Resin
TGM1A02-007 | Pipe Mount Clamp | PETG |  | FDM 3D Printing |  | 1 |  |  |  |  |  |  | PCB
TGM1A02-008 | Case Gasket | EPDM |  | Waterjet/manual |  | 1 |  |  |  |  |  |  | EVA
TGM1A02-009 | Ports Gasket | EPDM |  | Waterjet/manual |  | 1 |  |  |  |  |  |  | RTV Silicone
TGM1A02-010 | Acrylic LED/CAM Cover | Acrylic |  | Lasercut |  | 1
TGM1A02-011 | Ports Cover | Acrylic |  | Lasercut |  | 1
TGM1A02-012 | Battery Pack | Sourced | 8 cell Alkaline battery pack | Sourced Locally | https://robu.in/product/12v-8-x-aa-battery-clip-slot-holder-stack-box-case/ | 1 |  |  |  |  |  |  | EPDM
TGM1A02-013 | Knob Bolt | Sourced | M6x35 with knob | Sourced Locally | Example -https://www.mcmaster.com/2907T25/ | 1 |  |  |  |  |  |  | Acrylic
TGM1A02-014 | Nyloc Nut | Sourced | M6 Nyloc | Sourced Locally |  | 1
LT1A01-014 | Round Shell Connector 16mm | Sourced | 8 ways | Sourced Locally | Sunrom | 1 |  |  |  |  |  | Fabrication Process | Sourced Locally
LT1A01-016 | PCB Mounting Bolts | Sourced | M3x6 MS | Sourced Locally |  | 4 |  |  |  |  |  |  | Sourced Internationally
LT1A01-017 | Case Closure Bolts | Sourced | M4x14 SS | Sourced Locally |  | 9 |  |  | ₹6.6 | ₹59.4 |  |  | Lasercut
LT1A01-018 | Case Closure Inserts | Sourced | M4x4 Brass | Sourced Locally |  | 7 |  |  | ₹1.5 | ₹10.5 |  |  | Waterjet/manual
LT1A01-024 | M4 Wingnut | Sourced | M4 | Sourced Locally | Guptas | 3 |  | Wingbolts can be used too to replace three M4x14 bolts used for the covers. | ₹20 | ₹60 |  |  | Fabrication (In-House)
 |  |  |  |  |  |  |  |  |  |  |  |  | FDM 3D Printing
 |  |  |  |  |  |  |  |  |  |  |  |  | Vacuum Cast
 |  |  |  |  |  |  |  |  |  |  |  |  | Vacuum Formed
TGM1A03-000 | Device Frame
TGM1A03-001 | Frame Pipe Set | Sourced
TGM1A03-002 | Frame Panel Set | Sourced
TGM1A03-003 | Boom Clamps | PETG |  |  |  | 2
TGM1A03-004 | RFID Clamps
TGM1A01-004 | General Clamp | PETG |  | FDM 3D Printing |  | 19 |  | Used for mounting the MCU and Covers
TGM1A03-006
TGM1A03-007
 | Optional accessories
LT1A01-020 | Button Plug | RTV Silicone | Shore A40 | Vacuum Cast |  | 1
 | Expendables-
 | Loctite 406 | Sourced |  | Sourced Locally |  | 0.05
MC1A01-020 | Loctite SI 596 | Sourced |  | Sourced Locally | Zenith Chemicals or https://www.tryloctite.in/estore/gasketing-compounds-loctite-si-596-AD.GA.333670/ | 0.05 |  | Sourced |  | ₹320 | ₹16
 | Extras-
 | https://www.sunrom.com/p/pcb-spacers-6mm-heightt

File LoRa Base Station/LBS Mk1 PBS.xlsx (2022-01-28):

LoRa Base Station 1.2 - Product Breakdown Sheet |  |  |  |  |  |  |  |  | Pricing |  |  | Legend and Information
Part No. | Part Name | Material | Material Spec | Fabrication Process | Source | Qty. per Unit | Order Qty. | Remarks | Price Per Unit | Price per Product | Order Price | Part No. (#01-123) | LT1A10-001 = Main Model Number + Part Number Combined
LT1A00-000 | LoRa Base Station 1.2 Mk1 Rev1 |  |  |  |  | 1 | 40 |  |  | ₹8132.387728 | ₹0 |  | LT1A10-001 = Batch Number
LT1A01-000 | Enclosure |  |  |  |  |  |  |  |  |  |  |  | LT1A10-001 = Subassembly
LT1A01-001 | Case Shell | PETG |  | FDM 3D Printing |  | 1 |  |  | ₹1600 | ₹1600 |  |  | LT1A10-001 = Part Number
LT1A01-002 | OLED Windowpane | Acrylic | 2mm (actual 1.8mm) | Lasercut |  | 1 |  | Will be glued into place with Loctite 406 | ₹15.81967213 | ₹15.81967213 |  | Part Name | A name or identifier (eg- Driving Camshaft)
LT1A01-003 | Case Buttons Lip | PETG |  | FDM 3D Printing |  | 1 |  | Will be glued into place with Loctite 406 | ₹50 | ₹50 |  | Material
LT1A01-004 | Handles | PETG |  | FDM 3D Printing |  | 2 |  | Will be glued into place with Loctite 406 | ₹300 | ₹600 |  | Material Spec | material specifications, such as thickness or dimensions
LT1A01-005 | Case Lid | PETG |  | FDM 3D Printing |  | 1 |  |  | ₹800 | ₹800 |  | Process | Manufacturing Process (milling, routing, etc.)
LT1A01-006 | Case Seal | EPDM | 1mm | Waterjet/manual |  | 1 |  |  | ₹11.11111111 | ₹11.11111111 |  | Source | Specific manufacturer or Store to procure part from
LT1A01-007 | LT1 PCB | PCB |  | Sourced Locally | LionPCB/PCBPower | 1 |  | Cost here includes PCB + Electronics Estimate | ₹4588 | ₹4588 |  | Required Quantity | Quantity Required to build 1 unit
LT1A01-008 | SMA-KE Washer & Nut set | Sourced |  | Sourced Locally | Sunrom | 1 |  |  | ₹17 | ₹17 |  | Order Quantity | Total Quantity required including spares
LT1A01-009 | Button Caps | Sourced |  | Sourced Locally | Sunrom | 2 |  |  | ₹3.3 | ₹6.6 |  | Status | Denotes current state of part/s
LT1A01-010 | Button Cover | Acrylic | 5mm (actual 4.8mm) | Lasercut | Sunrom | 1 |  |  | ₹35.86111111 | ₹35.86111111 |  | Remarks | Additional notes or remarks
LT1A01-011 | Button Seal | EPDM | 1mm | Waterjet/manual |  | 1 |  |  | ₹5 | ₹5
LT1A01-012 | Ports Cover | Acrylic | 5mm (actual 4.8mm) | Lasercut |  | 1 |  |  | ₹34.39583333 | ₹34.39583333 |  | Stages of Completion | Unstarted
LT1A01-013 | Ports Seal | EPDM | 1mm | Waterjet/manual |  | 1 |  |  | ₹4 | ₹4 |  |  | In CAD
LT1A01-014 | Round Shell Connector | Sourced | 16mm Dia | Sourced Locally |  | 1 |  |  | ₹79 | ₹79 |  |  | CAD Completed
LT1A01-015 | Round Shell Dust Cap | Sourced |  | Sourced Locally |  | 1 |  |  | ₹16 | ₹16 |  |  | Prototyping
LT1A01-016 | PCB Mounting Bolts | Sourced | M3x6 MS | Sourced Locally |  | 5 |  |  | ₹1.0 | ₹5 |  |  | Manufacturing
LT1A01-017 | Case Closure Bolts | Sourced | M4x14 SS | Sourced Locally |  | 10 |  |  | ₹6.6 | ₹66 |  |  | To Be Sourced
LT1A01-018 | Case Closure Inserts | Sourced | M4x4 Brass | Sourced Locally |  | 10 |  |  | ₹1.5 | ₹15 |  |  | Sourced
LT1A01-019 | Cover Fastener Circlips | Sourced | E-type circlip A4 | Sourced Locally |  | 3 |  | E-type | ₹2 | ₹6 |  |  | Needs Assembly
LT1A01-020 | Fastener Rubber Washer | Sourced | 4mm ID, 8mm OD, 1mm CS | Sourced Locally |  | 10 |  | Buy 1.2x required, some have issues with poor moulding. | ₹2 | ₹20 |  |  | Assembled
LT1A01-021 | OLED Spacer | Sourced | 4.5mm | Sourced Locally |  | 4 |  |  | ₹0.9 | ₹3.6
LT1A01-022 | OLED Bolts | Sourced | M2x10 | Sourced Locally |  | 4 |  | This can be replaced with M3x10 if the PCB is redrilled | ₹3 | ₹12 |  | Materials | Stainless Steel Sheet
LT1A01-023 | OLED Nuts | Sourced | M2 | Sourced Locally |  | 4 |  | This can be replaced with M3x10 if the PCB is redrilled | ₹2 | ₹8 |  |  | Baltic Birch Ply
LT1A01-024 | M4 Wingnut | Sourced | M4 | Sourced Locally | Guptas | 3 |  | Wingbolts can be used too to replace three M4x14 bolts used for the covers. | ₹2 | ₹6 |  |  | Sourced
 |  |  |  |  |  |  |  |  |  |  |  |  | EPDM
LT1A02-001 | Backplate | Acrylic | 5mm (actual 4.8mm) | Lasercut |  | 1 |  |  | ₹128 | ₹128 |  |  | Acrylic
LT1A02-002 | Foam | EVA | 6mm | Lasercut |  | 1 |  |  | ₹41.66666667 | ₹41.66666667 |  |  | PETG
 |  |  |  |  |  |  |  |  |  |  |  |  | Resin
LT1A03-001 | Stevenson Screen | PETG |  | FDM 3D Printing |  | 1 |  | Can be tentatively FDM printed, will experiment with vacuum forming shortly |  | ₹0 |  |  | PCB
LT1A03-002 | Bolts | Sourced | M4x8 SS | Sourced Locally |  | 4 |  |  | ₹4.8 | ₹19.2 |  |  | EVA
LT1A03-003 | Nuts | Sourced | M4 SS | Sourced Locally |  | 4 |  |  | ₹1.6 | ₹6.4 |  |  | RTV Silicone
LT1A03-004 | Washers | Sourced | M4 SS | Sourced Locally |  | 4 |  |  | ₹3 | ₹12
 | Optional accessories |  |  |  |  |  |  |  |  |  |  |  | EPDM
LT1A04-001 | Button Plug | RTV Silicone | Shore A40 | Vacuum Cast |  | 1 |  |  | ₹30 | ₹30 |  |  | Acrylic
LT1A04-002 | Ports Plug | RTV Silicone | Shore A40 | Vacuum Cast |  | 1 |  |  | ₹25 | ₹25
 |  |  |  |  |  |  |  |  |  |  |  | Fabrication Process | Sourced Locally
 | Expendables- |  |  |  |  |  |  |  |  |  |  |  | Sourced Internationally
LT1A01-020 | Loctite 406 | Sourced |  | Sourced Locally |  | 0.05 |  |  | ₹320 | ₹16 |  |  | Lasercut
 |  |  |  |  |  |  |  |  |  |  |  |  | Waterjet/manual
 |  |  |  |  |  |  |  |  |  |  |  |  | Fabrication (In-House)
 | Extras- |  |  |  |  |  |  |  |  |  |  |  | FDM 3D Printing
 | https://www.evelta.com/solar-power-management-module-for-6v-24v-solar-panel/ |  |  |  |  |  |  |  |  |  |  |  | Vacuum Cast
 | https://www.sunrom.com/p/plastic-pcb-spacer-with-adhesive-base-for-34mm-holes |  |  |  |  |  |  |  |  |  |  |  | Vacuum Formed
 | https://www.sunrom.com/p/pcb-spacers-6mm-heightt

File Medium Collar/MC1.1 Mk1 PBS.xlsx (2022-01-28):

MediumCollar1.1 - Product Breakdown Sheet |  |  |  |  |  |  |  |  |  | Pricing |  |  | Legend and Information
Part No. | Part Name | Material | Material Spec | Fabrication Process | Source | Qty. per Unit | Order Qty. | Stage | Remarks | Price Per Unit | Price per Product | Order Price | Part No. (#01-123) | MC1A10-001 = Main Model Number + Part Number Combined
MC1A00-000 | MediumCollar1.1 Mk1 (Electronic Release) |  |  |  |  | 1 | 40 | CAD Completed |  |  | ₹1454 | ₹0 |  | MC1A10-001 = Batch Number
MC1A01-000 | Collar unit |  |  |  |  |  |  | CAD Completed |  |  |  |  |  | MC1A10-001 = Subassembly
MC1A01-001 | Type C Case C1.1 | PETG |  | FDM 3D Printing |  | 1 |  | CAD Completed | Type C is for the ballchain/wire inside a 7mm rubber tube | ₹360 | ₹360 |  |  | MC1A10-001 = Part Number
MC1A01-002 | Type C Lid | PETG |  |  |  | 1 |  | CAD Completed |  | ₹80 | ₹80 |  | Part Name | A name or identifier (eg- Driving Camshaft)
MC1A01-003 | MC1 PCB | PCB |  |  |  | 1 |  | CAD Completed |  |  | ₹0 |  | Material
MC1A01-004 | LS14500 | Sourced | LS14500 (tab termination) |  | SAFT (through Manoj) | 1 |  | Sourced |  | 475 | ₹475 |  | Material Spec | material specifications, such as thickness or dimensions
MC1A01-005 | Plastite Screws CSK | Sourced | B4B6703010 |  | JC Gupta & Sons | 5 |  | Sourced |  | 5.6 | ₹28 |  | Process | Manufacturing Process (milling, routing, etc.)
MC1A01-006 | Magnet | Sourced |  |  |  | 1 |  | Sourced | Magnet to be taped opposite the open end of the MC1 case, to keep the device deactivated until in use. |  | ₹0 |  | Source | Specific manufacturer or Store to procure part from
MC1A01-007 | Mini M10 Motor | Sourced |  |  |  | 1 |  | Sourced | For the motor release | 212 | ₹212 |  | Required Quantity | Quantity Required to build 1 unit
MC1A01-008 | Release Case | PETG |  |  |  | 1 |  | Sourced | Smaller components | 80 | ₹80 |  | Order Quantity | Total Quantity required including spares
MC1A01-009 | Release Lid | PETG |  |  |  | 1 |  | Sourced |  | 50 | ₹50 |  | Status | Denotes current state of part/s
MC1A01-010 | Shackle | PETG |  |  |  | 1 |  | Sourced |  | 15 | ₹15 |  | Remarks | Additional notes or remarks
MC1A01-011 | Latch | PETG |  |  |  | 1 |  | Sourced |  | 5 | ₹5
MC1A01-012 | Steel wire rope | Sourced | 2mm 7*7 cable |  |  | 1 |  | Sourced |  | 9 | ₹9 |  | Stages of Completion | Unstarted
MC1A01-013 | Collar tubing | Sourced | Rubber tube 2mm ID 4-8mm OD |  |  | 1 |  | To Be Sourced |  |  | ₹0 |  |  | In CAD
MC1A01-014 | Grub screws | Sourced | M3*6 |  |  | 2 |  | Sourced | Used to retain the Steel wire rope | ₹3 | ₹6 |  |  | CAD Completed
MC1A01-015 | Motor Driver PCB | PCB |  |  | Robokits | 1 |  | Sourced | https://robokits.co.in/motor-drives-drivers/dc-motor-driver/two-way-motor-drive-module-drv8833 | 98 | ₹98 |  |  | Prototyping
MC1A01-016 | Roller Bearing | Sourced | 5.12x7.9mm (DxH) |  | Kashyap's | 1 |  | Sourced |  | 20 | ₹20 |  |  | Manufacturing
 |  |  |  |  |  |  |  |  |  |  |  |  |  | To Be Sourced
 | Expendables- |  |  |  |  |  |  |  |  |  |  |  |  | Sourced
MC1A01-020 | Loctite SI 596 | Sourced |  | Sourced Locally | Zenith Chemicals or https://www.tryloctite.in/estore/gasketing-compounds-loctite-si-596-AD.GA.333670/ | 0.05 |  | Sourced |  | ₹320 | ₹16 |  |  | Needs Assembly
 |  |  |  |  |  |  |  |  |  |  |  |  |  | Assembled
 | Extras- |  |  |  |  |  |  |  |  |  |  |  | Materials | Stainless Steel Sheet
 |  |  |  |  |  |  |  |  |  |  |  |  |  | Baltic Birch Ply
 |  |  |  |  |  |  |  |  |  |  |  |  |  | Sourced
 |  |  |  |  |  |  |  |  |  |  |  |  |  | EPDM
 |  |  |  |  |  |  |  |  |  |  |  |  |  | Acrylic
 |  |  |  |  |  |  |  |  |  |  |  |  |  | PETG
 |  |  |  |  |  |  |  |  |  |  |  |  |  | Resin
 |  |  |  |  |  |  |  |  |  |  |  |  |  | PCB
 |  |  |  |  |  |  |  |  |  |  |  |  |  | EVA
 |  |  |  |  |  |  |  |  |  |  |  |  | Fabrication Process | Sourced Locally
 |  |  |  |  |  |  |  |  |  |  |  |  |  | Sourced Internationally
 |  |  |  |  |  |  |  |  |  |  |  |  |  | Lasercut
 |  |  |  |  |  |  |  |  |  |  |  |  |  | Waterjet/manual
 |  |  |  |  |  |  |  |  |  |  |  |  |  | Fabrication (In-House)
 |  |  |  |  |  |  |  |  |  |  |  |  |  | FDM 3D Printing
 |  |  |  |  |  |  |  |  |  |  |  |  |  | Vacuum Cast
 |  |  |  |  |  |  |  |  |  |  |  |  |  | Vacuum Formed

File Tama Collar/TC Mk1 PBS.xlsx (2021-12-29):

TamaCollar1.1A - Product Breakdown Sheet |  |  |  |  |  |  |  |  |  | Pricing |  |  | Legend and Information
Part No. | Part Name | Material | Material Spec | Fabrication Process | Source | Qty. per Unit | Order Qty. | Stage | Remarks | Price Per Unit | Price per Product | Order Price | Part No. (#01-123) | MC1A10-001 = Main Model Number + Part Number Combined
TC1A00-000 | TamaCollar1.1A Mk1 |  |  |  |  | 1 | 40 | Manufacturing |  |  | ₹842 | ₹0 |  | MC1A10-001 = Batch Number
TC1A01-001 | TC1 Case | ABS |  | Vacuum Formed |  | 1 |  | Manufacturing |  | ₹173 | ₹173 |  |  | MC1A10-001 = Subassembly
TC1A01-002 | TC1 Lid | ABS |  | Vacuum Formed |  | 1 |  | Manufacturing |  | ₹173 | ₹173 |  |  | MC1A10-001 = Part Number
TC1A01-003 | TC1 PCB | PCB |  |  |  | 1 |  | Manufacturing |  |  | ₹0 |  | Part Name | A name or identifier (eg- Driving Camshaft)
TC1A01-004 | CP502525 | Sourced |  |  |  | 1 |  | Sourced |  | 475 | ₹475 |  | Material
TC1A01-005 | Ball Chain | Sourced |  |  |  |  |  | Sourced |  |  |  |  | Material Spec | material specifications, such as thickness or dimensions
TC1A01-006 | Magnet | Sourced |  |  |  |  |  | Sourced | Used to disconnect the battery |  |  |  | Process | Manufacturing Process (milling, routing, etc.)
TC1A01-007 | LoRa Antenna | Sourced | 1mm Fibreglass-covered wire |  |  | 1 | 1 | Sourced | Length required will vary depending on frequency | 5 | ₹5 |  | Source | Specific manufacturer or Store to procure part from
 |  |  |  |  |  |  |  |  |  |  |  |  | Required Quantity | Quantity Required to build 1 unit
 |  |  |  |  |  |  |  |  |  |  |  |  | Order Quantity | Total Quantity required including spares
 |  |  |  |  |  |  |  |  |  |  |  |  | Status | Denotes current state of part/s
 | Expendables- |  |  |  |  |  |  |  |  |  |  |  | Remarks | Additional notes or remarks
MC1A01-020 | Loctite 406 | Sourced |  | Sourced Locally | Zenith Chemicals or https://www.tryloctite.in/estore/gasketing-compounds-loctite-si-596-AD.GA.333670/ | 0.05 |  | Sourced |  | ₹320 | ₹16
 |  |  |  |  |  |  |  |  |  |  |  |  | Stages of Completion | Unstarted
 |  |  |  |  |  |  |  |  |  |  |  |  |  | In CAD
 | Extras- |  |  |  |  |  |  |  |  |  |  |  |  | CAD Completed
 |  |  |  |  |  |  |  |  |  |  |  |  |  | Prototyping
 |  |  |  |  |  |  |  |  |  |  |  |  |  | Manufacturing
 |  |  |  |  |  |  |  |  |  |  |  |  |  | To Be Sourced
 |  |  |  |  |  |  |  |  |  |  |  |  |  | Sourced
 |  |  |  |  |  |  |  |  |  |  |  |  |  | Needs Assembly
 |  |  |  |  |  |  |  |  |  |  |  |  |  | Assembled
 |  |  |  |  |  |  |  |  |  |  |  |  | Materials | Stainless Steel Sheet
 |  |  |  |  |  |  |  |  |  |  |  |  |  | Baltic Birch Ply
 |  |  |  |  |  |  |  |  |  |  |  |  |  | Sourced
 |  |  |  |  |  |  |  |  |  |  |  |  |  | EPDM
 |  |  |  |  |  |  |  |  |  |  |  |  |  | Acrylic
 |  |  |  |  |  |  |  |  |  |  |  |  |  | ABS
 |  |  |  |  |  |  |  |  |  |  |  |  |  | Resin
 |  |  |  |  |  |  |  |  |  |  |  |  |  | PCB
 |  |  |  |  |  |  |  |  |  |  |  |  |  | EVA
 |  |  |  |  |  |  |  |  |  |  |  |  | Fabrication Process | Sourced Locally
 |  |  |  |  |  |  |  |  |  |  |  |  |  | Sourced Internationally
 |  |  |  |  |  |  |  |  |  |  |  |  |  | Lasercut
 |  |  |  |  |  |  |  |  |  |  |  |  |  | Waterjet/manual
 |  |  |  |  |  |  |  |  |  |  |  |  |  | Fabrication (In-House)
 |  |  |  |  |  |  |  |  |  |  |  |  |  | FDM 3D Printing
 |  |  |  |  |  |  |  |  |  |  |  |  |  | Vacuum Cast
 |  |  |  |  |  |  |  |  |  |  |  |  |  | Vacuum Formed

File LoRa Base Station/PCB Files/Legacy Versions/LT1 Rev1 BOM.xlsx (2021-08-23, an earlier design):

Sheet: BOM
Initial Run Units- | 11 | Note, some components like caps will need larger order quantities |  |  |  |  | ECAD Version- v26
Order Quantity | Qty | Value | Package | Parts | Description | CATEGORY | LINK
11 | 1 |  | BATTCOM_20MM_PTH | BACKUP_BATT1 | Battery - Single Cell |  | https://www.evelta.com/3v-litium-battery-holder/
11 | 1 |  | SMA_EDGELAUNCH | SMA | SMA Connector
55 | 5 | 0.1uF | CAPC2012X110 | C3, C4, C5, C7, C14 | Capacitor - Generic | Capacitor | https://www.sunrom.com/p/100nf-104-smd-0805-pack-of-20
11 | 1 | 0.96_OLED_I2C | OLED_0.96_I2C | OLED1 |  |  | https://www.module143.com/0.96inch-i2c-oled-module
11 | 1 | 100uF | CAP_2P_5X11 | C10 | Capacitor Polarised - Generic |  | https://www.evelta.com/100uf-25v-electrolytic-capacitor/
44 | 4 | 10k | RESC2012X65 | R3, R4, R5, R6 | Resistor Fixed - Generic | Resistor | https://www.sunrom.com/p/10k-1-0805-pack-of-100
11 | 1 | 10uF | CAPC2012X110 | C8, C9 | Capacitor - Generic | Capacitor | https://www.sunrom.com/p/10uf-106-smd-0805-pack-of-10
11 | 1 | 1N5820 | SODFL3718X115 | D1 | Schottky Diode - Popular parts |  | https://www.sunrom.com/p/1n5819-b5819w-1n5819w-s4-sod123-1206-1a-40v-schottky-diode
11 | 1 | 1P2T_SLIDE_SWITCH | 1P2T_SLIDE_SWITCH | S1 |  |  | https://www.sunrom.com/p/slide-switch-1p2t-high-current-straight
33 | 3 | 1uF | CAPC2012X110 | C11, C12, C13 | Capacitor - Generic | Capacitor | https://www.sunrom.com/p/1uf-105-smd-0805-pack-of-10
22 | 2 | 33pF | CAPC2012X110 | C1, C2 | Capacitor - Generic | Capacitor | https://www.evelta.com/33-pf-50v-0805-smd-multilayer-ceramic-capacitors-0805cg330j500nt-fenghua/
22 | 2 | 4.7k | RESC2012X65 | R1, R2 | Resistor Fixed - Generic | Resistor | https://www.sunrom.com/p/4k7-1-0805-pack-of-100
11 | 1 | 4.7uF | CAPC2012X110 | C6 | Capacitor - Generic | Capacitor | https://www.evelta.com/4-7-uf-16v-0805-smd-multi-layer-ceramic-capacitor-0805x475k160ct-walsin/
11 | 1 | 470uF | CAP_5P_10X12.5 | C15 | Capacitor Polarised - Generic |  | https://www.evelta.com/470uf-25v-electrolytic-capacitor/
11 | 1 | 68uh | INDUCTOR_12X12MM | L1 |  |  | https://www.sunrom.com/p/68uh-680-12mm-inductor
11 | 1 | 8mhz | HC49UP | Q1 | CRYSTAL |  | https://www.evelta.com/hc-49smd-8mhz-20pf-20ppm-2pad-smd-smt-quartz-crystal/
11 | 1 | ATMEGA328P-AU | QFP32_7X7_0.80 | U1 | 8-bit AVR Microcontroller |  | https://www.evelta.com/atmega328p-au-ic-mcu-8bit-32kb-flash-32tqfp/
11 | 1 | DS3231MZ+ | DS3231MZ+_SOIC8 | U5 |  |  | https://www.evelta.com/ds3231mz-maxim-integrated-alarm-rtc-i2c-2-3-v-to-5-5-v/
11 | 1 | PMOSFET | PMOSFET_SOT23 | U3 |  | P-Channel MOSFET - Generic | https://www.sunrom.com/p/ao3401-a19t-sot-23-p-ch-mosfet
11 | 1 | LDO-LM11173.3MP | SOT223 | P2 | 800mA Low-Dropout Linear Regulator |  | https://www.sunrom.com/m/4004
11 | 1 | LORA_RFM95W-915S2_MODULE | LORA_RFM95W-915S2_16MODULE | U4 |  |  | https://www.digikey.in/product-detail/en/rf-solutions/RFM95W-915S2/RFM95W-915S2-ND/6564923
22 | 2 | MOMENTARY-SWITCH-SPST-PTH-12MM | TACTILE_SWITCH_PTH_12MM | S2, S3 | Momentary Switch (Pushbutton) - SPST |  | https://www.sunrom.com/p/tactile-switch-square-head-omron-b3f-4055-12x12x73mm
11 | 1 | MOMENTARY-SWITCH-SPST-PTH-6MM |  | S4 | Momentary Switch (Pushbutton) - SPST |  | https://www.sunrom.com/p/tactile-switch-6x6x43mm
11 | 1 | PA6H_GPS | PA6H_GPS-MODULE_20PIN | U2 |  |  | https://www.rhydolabz.com/wireless-gps-c-130_186/gps-smd-module-with-antennapa6h-p-1911.html
11 | 1 | SD_MICRO_SOCKET-204270SD_FULL | SD_CARD_SOCKET-794212 | SD |  |  | https://www.sunrom.com/p/full-sd-card-socket
22 | 2 | TERMINAL_BLOCK | TERM_BLOCK_2PIN_7.62MM | JP3A, JP4A, JP5A |  |  | https://www.sunrom.com/p/screw-terminal-2-pin
11 | 1 | XL1509 | XL1509_SOIC8 | P1 |  |  | https://www.sunrom.com/m/6161
11 | 1 | DC Power Jack |  | J1 |  |  | https://www.sunrom.com/p/dc-socket
 |  | SMA-KE connectors
11 | 1 | https://inkocean.in/products/1-6-partial-foot-extension-sma-sma-ke-radio-base-screw-hole-in-the-outer-tooth-profile-coaxial-connector-11mm |  |  |  |  | Remark- both these connectors are seemingly identical, hence I've included both links to be ordered at your discretion.
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

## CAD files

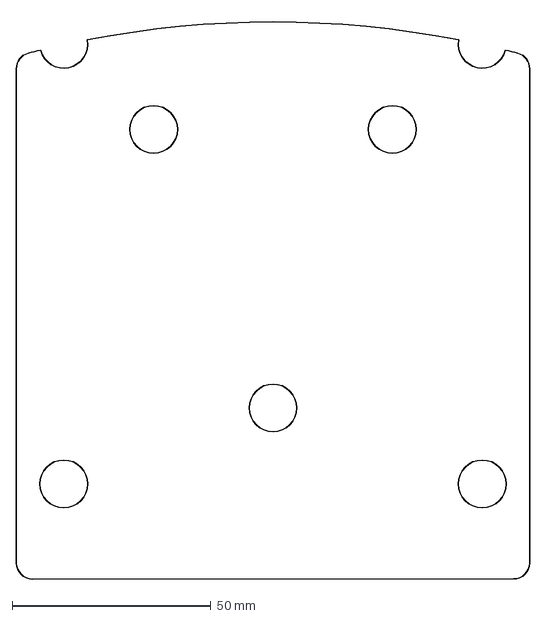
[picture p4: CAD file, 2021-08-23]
LoRa Base Station/Hardware Files/Lasercutting Profiles/EVA Foam 5mm Backplate Foam.dxf
129.0 x 141.5 mm

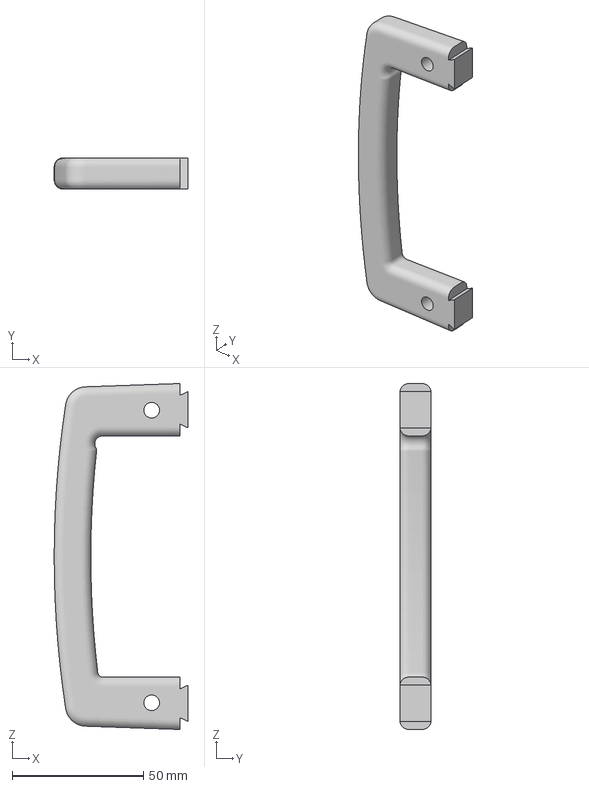
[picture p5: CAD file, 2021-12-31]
LoRa Base Station/Hardware Files/PETG Handle (qty x2).3mf
51.0 x 12.0 x 132.0 mm

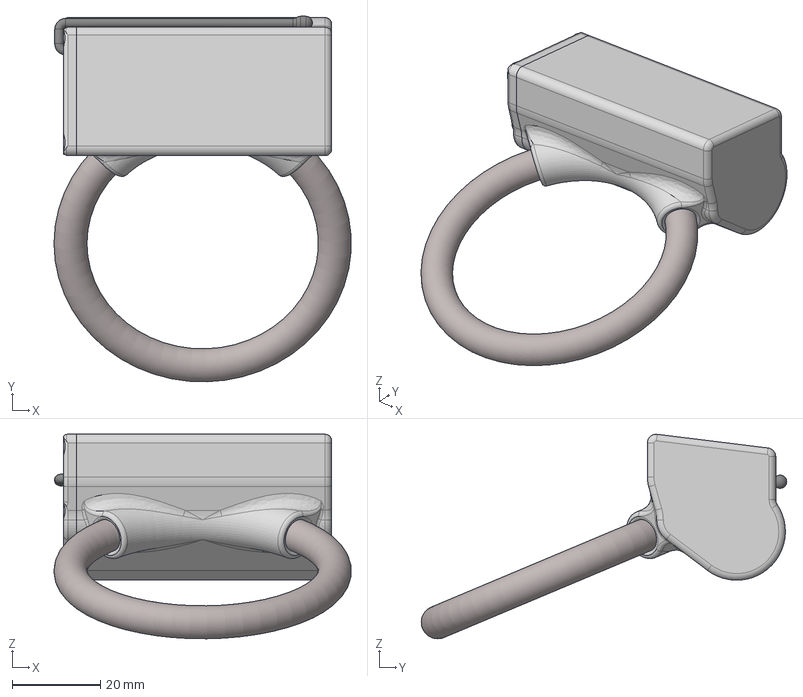
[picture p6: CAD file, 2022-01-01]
Medium Collar/Hardware Files/MediumCollar1 (Degradable Release)/MediumCollar1 Type C v30.step
67.4 x 83.0 x 46.4 mm
Top Packages
Bottom Packages
AA Battery Dummy
95893A191_Flat Head Thread-Forming Screws for Plastic (1) x 5

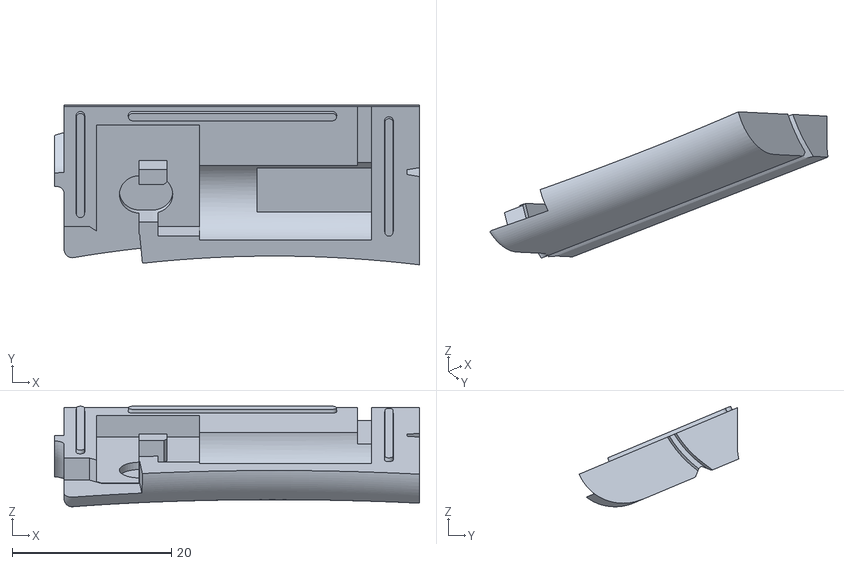
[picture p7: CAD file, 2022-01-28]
Medium Collar/Hardware Files/MediumCollar1.1 (Electronic Release)/Release Case.stl
45.8 x 20.0 x 12.6

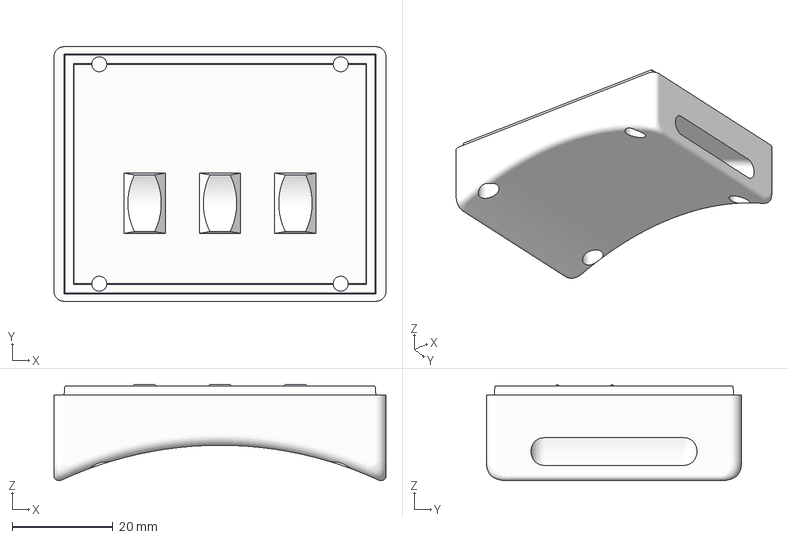
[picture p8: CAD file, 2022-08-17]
Medium Collar/Hardware Files/MediumCollar1.1 (Belt, C-Cell)/MC1.1 Type A Tubular C-cell Lid (Curved Type).3mf
66.0 x 50.6 x 19.2 mm

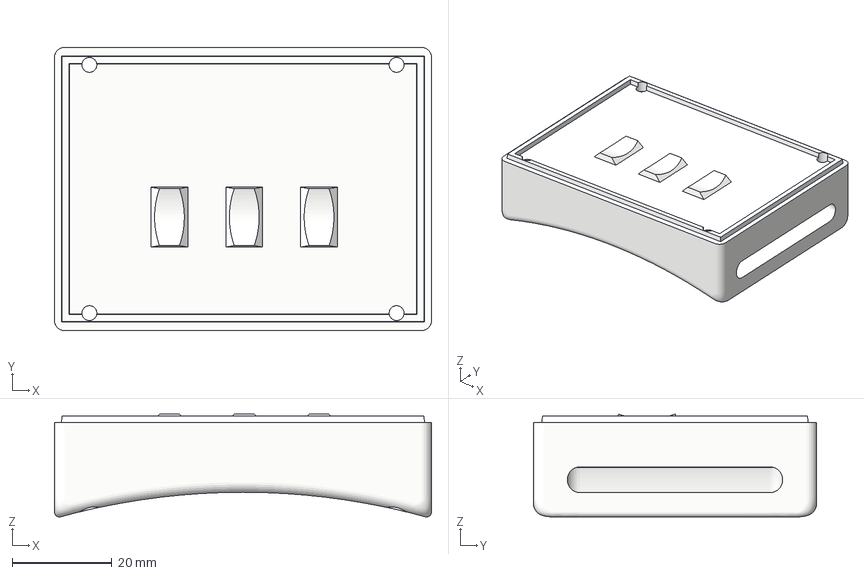
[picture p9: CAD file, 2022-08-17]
Medium Collar/Hardware Files/MediumCollar1.1A (Belt, D-Cell)/MC1.1 Type A Tubular D-cell(Thin Case)/MC1.1 Type A Tubular D-cell(Thin Case) Lid (Curved Type).3mf
75.6 x 56.8 x 20.6 mm

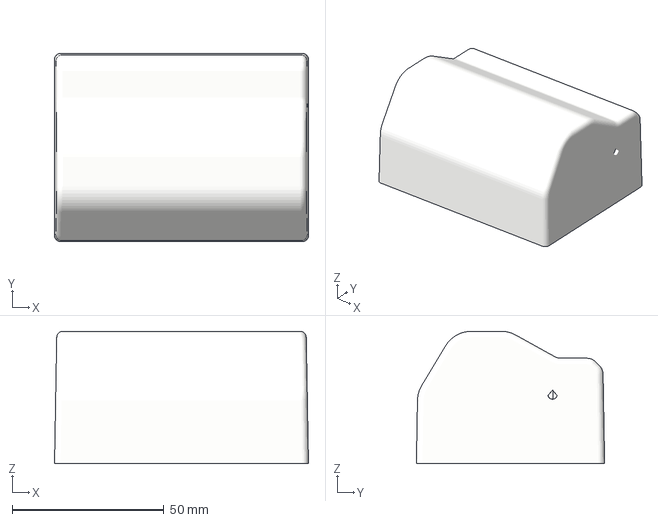
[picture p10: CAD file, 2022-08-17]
Medium Collar/Hardware Files/MediumCollar1.1A (Belt, D-Cell)/MC1.1 Type A Tubular D-cell.3mf
83.6 x 62.0 x 43.6 mm

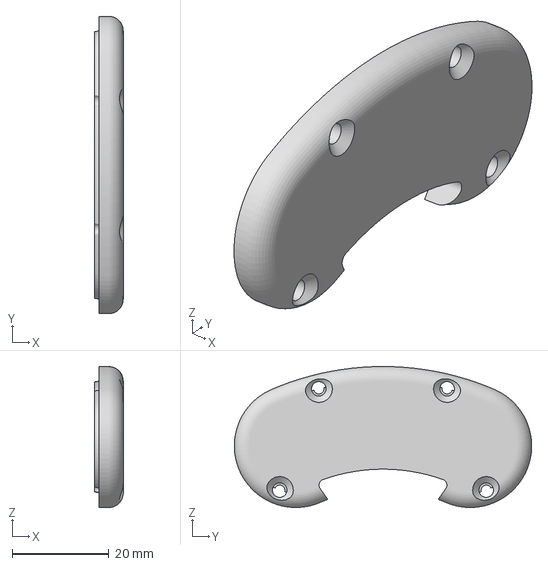
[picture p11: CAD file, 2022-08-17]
Medium Collar/Hardware Files/MediumCollar1.1D (Backpack Harness)/MC1 Type D Backpack Lid.3mf
5.90 x 61.4 x 29.1 mm

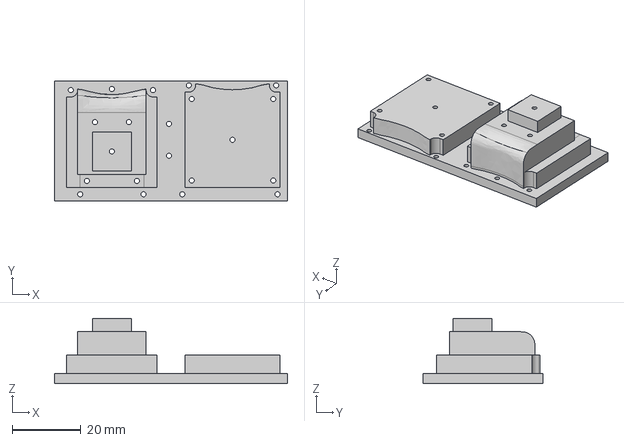
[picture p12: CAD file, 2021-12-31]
Tama Collar/Hardware Files/TC1 TypeD Buck.step
68.0 x 35.0 x 19.1 mm

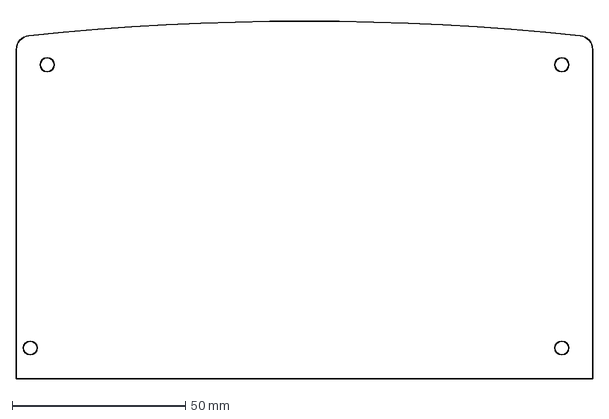
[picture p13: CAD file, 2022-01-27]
Tamarin Group Monitor/Hardware Files/Cam Case Gasket PProf.dxf
166.5 x 104.7 mm

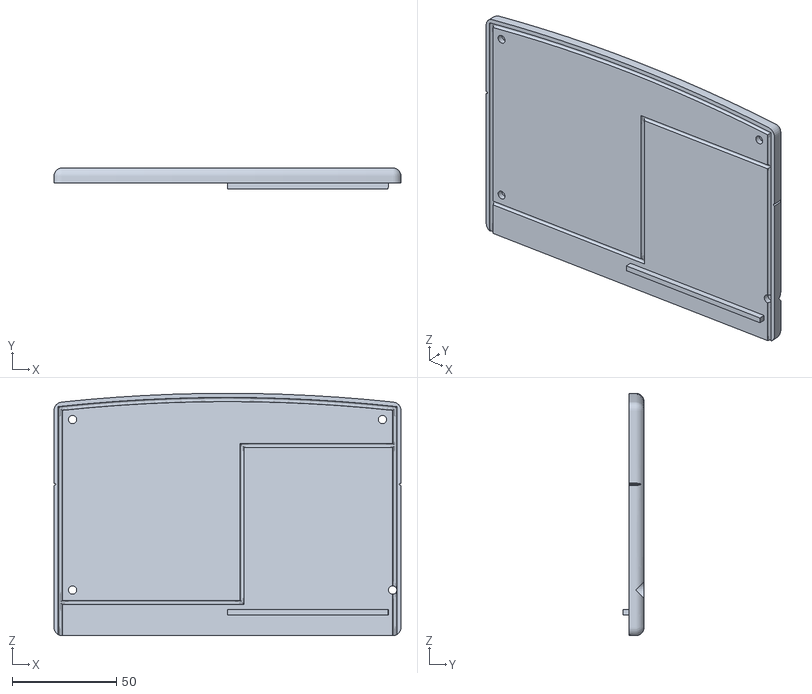
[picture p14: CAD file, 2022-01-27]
Tamarin Group Monitor/Hardware Files/Camera Unit/Case Cover.stl
166.5 x 10.2 x 116.3

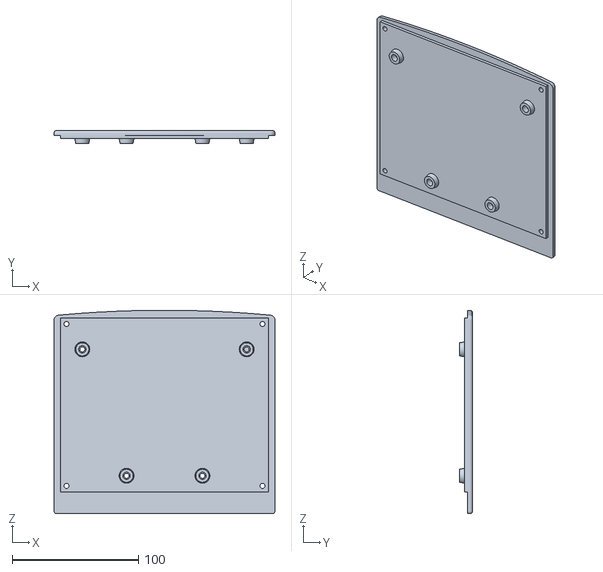
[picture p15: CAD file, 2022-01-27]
Tamarin Group Monitor/Hardware Files/MCU Unit/Case Cover.stl
174.8 x 10.4 x 160.9

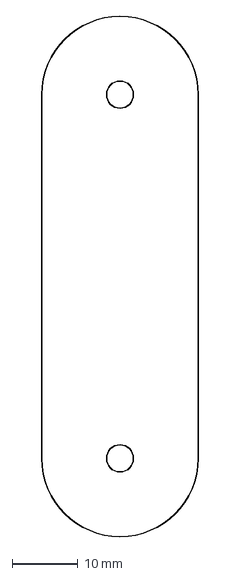
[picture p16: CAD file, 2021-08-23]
LoRa Base Station/Hardware Files/Lasercutting Profiles/Acrylic 5mm Button Cover.dxf
23.8 x 79.1 mm

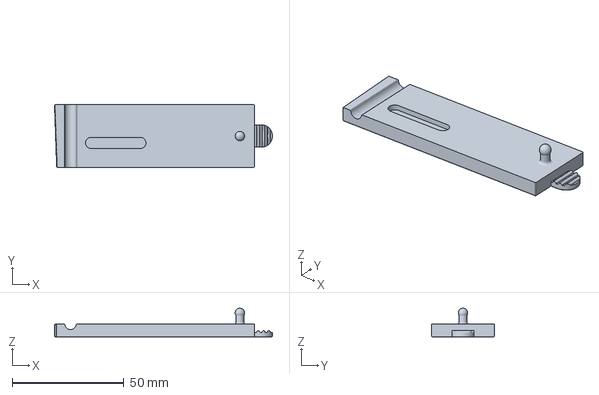
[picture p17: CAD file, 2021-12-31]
LoRa Base Station/Hardware Files/TPU Ports Bathplug.3mf
97.4 x 28.0 x 12.8 mm

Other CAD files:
Medium Collar/Hardware Files/MediumCollar1 (Degradable Release)/MediumCollar1 Case C.stl
Medium Collar/Hardware Files/MediumCollar1.1 (Electronic Release)/MC1.1 Release Mech.stl
Medium Collar/Hardware Files/MediumCollar1.1 (Belt, C-Cell)/MC1.1 Type A Tubular C-cell.3mf
Medium Collar/Hardware Files/MediumCollar1.1A (Belt, D-Cell)/MC1.1 Type A Tubular D-cell Lid(Curved Type).3mf
LoRa Base Station/Hardware Files/Lasercutting Profiles/Acrylic 2mm Window.dxf
LoRa Base Station/Hardware Files/Lasercutting Profiles/Acrylic 5mm Ports Cover.dxf
LoRa Base Station/Hardware Files/Lasercutting Profiles/Acrylic 6mm Backplate.dxf
LoRa Base Station/Hardware Files/Lasercutting Profiles/EPDM 1mm Button Seal.dxf
LoRa Base Station/Hardware Files/Lasercutting Profiles/EPDM 1mm Case Seal.dxf
LoRa Base Station/Hardware Files/Lasercutting Profiles/EPDM 1mm Ports Seal.dxf
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

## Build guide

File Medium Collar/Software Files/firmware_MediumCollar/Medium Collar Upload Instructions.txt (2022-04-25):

Medium Collar
These are steps for SPI
Step 1 Reset
".\avrdude" -C avrdude.conf -c stk500v1 -P COM7 -b 19200 -p atmega328p reset

Step 2 Set Fuse Bits
".\avrdude" -C avrdude.conf -c stk500v1 -P COM7 -b 19200 -p atmega328p -U lfuse:w:0xE2:m -U hfuse:w:0xD8:m -U efuse:w:0xFF:m

Step 3 Reset
".\avrdude" -C avrdude.conf -c stk500v1 -P COM7 -b 19200 -p atmega328p reset

Step 4 Upload Bootloader
".\avrdude" -C avrdude.conf -c stk500v1 -P COM7 -b 19200 -p atmega328p -e -U flash:w:bootloader/optiboot_atmega328_8.hex:i

Step 5 Reset
".\avrdude" -C avrdude.conf -c stk500v1 -P COM7 -b 19200 -p atmega328p reset

Step for FTDI
Step 1 Reset
Win Command: ".\avrdude" -C avrdude.conf -c arduino -P COM5 -b 19200 -p atmega328p reset
Mac Command: avrdude -c arduino -P /dev/tty.usbserial-A50285BI -b 19200 -p atmega328p reset

Step 2 Upload Firmware
Win Command: ".\avrdude" -C avrdude.conf -c arduino -P COM5 -b 19200 -p atmega328p -e -U flash:w:Build_mc/medium_collar.hex:i
Mac Command: avrdude -c arduino -P /dev/tty.usbserial-A50285BI -b 19200 -p atmega328p -e -U flash:w:Build_mc/medium_collar.hex:i

Step 3 Reset
".\avrdude" -C avrdude.conf -c arduino -P COM5 -b 19200 -p atmega328p reset

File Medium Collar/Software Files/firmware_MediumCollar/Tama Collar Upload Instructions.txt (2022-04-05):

Tama Collar 
These are steps for SPI
Step 1 Reset
".\avrdude" -C avrdude.conf -c stk500v1 -P COM7 -b 19200 -p atmega328p reset

Step 2 Set Fuse Bits
".\avrdude" -C avrdude.conf -c stk500v1 -P COM7 -b 19200 -p atmega328p -U lfuse:w:0xfd:m -U hfuse:w:0xd8:m -U efuse:w:0xff:m

Step 3 Reset
".\avrdude" -C avrdude.conf -c stk500v1 -P COM7 -b 19200 -p atmega328p reset

Step 4 Upload Bootloader
".\avrdude" -C avrdude.conf -c stk500v1 -P COM7 -b 19200 -p atmega328p -e -U flash:w:bootloader/optiboot_atmega328_4.hex:i

Step 5 Reset
".\avrdude" -C avrdude.conf -c stk500v1 -P COM7 -b 19200 -p atmega328p reset

Step for FTDI
Step 1 Reset
Win Cmd: ".\avrdude" -C avrdude.conf -c arduino -P COM5 -b 19200 -p atmega328p reset
Mac Cmd: avrdude -c arduino -P /dev/tty.usbserial-A50285BI -b 19200 -p atmega328p reset

Step 2 Upload Firmware
Win Cmd: ".\avrdude" -C avrdude.conf -c arduino -P COM5 -b 19200 -p atmega328p -e -U flash:w:Build/tama_collar.hex:i
Mac Cmd: avrdude -c arduino -P /dev/tty.usbserial-A50285BI -b 19200 -p atmega328p -e -U flash:w:Build/tama_collar.hex:i

Step 3 Reset
".\avrdude" -C avrdude.conf -c arduino -P COM5 -b 19200 -p atmega328p reset

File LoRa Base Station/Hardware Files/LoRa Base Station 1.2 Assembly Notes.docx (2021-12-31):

# LoRa Base Station 1.2 Assembly Notes

# Enclosure Shell Assembly Order

1. Check if all supports are clean and removed. Use a twist drill bit by hand to clean out any supports in holes.
2. Use a 7mm drill bit to clean up SMA connector hole.
3. Check OLED window fit, apply glue to edges of acrylic and reinsert into place
4. Check button plate fit, apply glue to edges and insert into place. Additional glue around inside edges if desired.
5. Insert 7 brass fasteners into shell using a 40w soldering iron for heat and the flattening technique. https://hackaday.com/2019/02/28/threading-3d-printed-parts-how-to-use-heat-set-inserts/

# Lid Assembly order

1. Insert 3 brass fasteners into lid using a 40w soldering iron for heat and the flattening technique. https://hackaday.com/2019/02/28/threading-3d-printed-parts-how-to-use-heat-set-inserts/
2. If the lid EPDM gasket is not cut, use the lasercut stencil to trace out the profile of the gasket, and cut with an xacto-style blade or scalpel. Use repeated shallow passes.
3. Ensure fit of lid gasket, and glue into position using Loctite 406.

# PCB Insertion

1. Note- There is a notch in the upper portion of the shell to push the PCB into while inserting the SMA connector

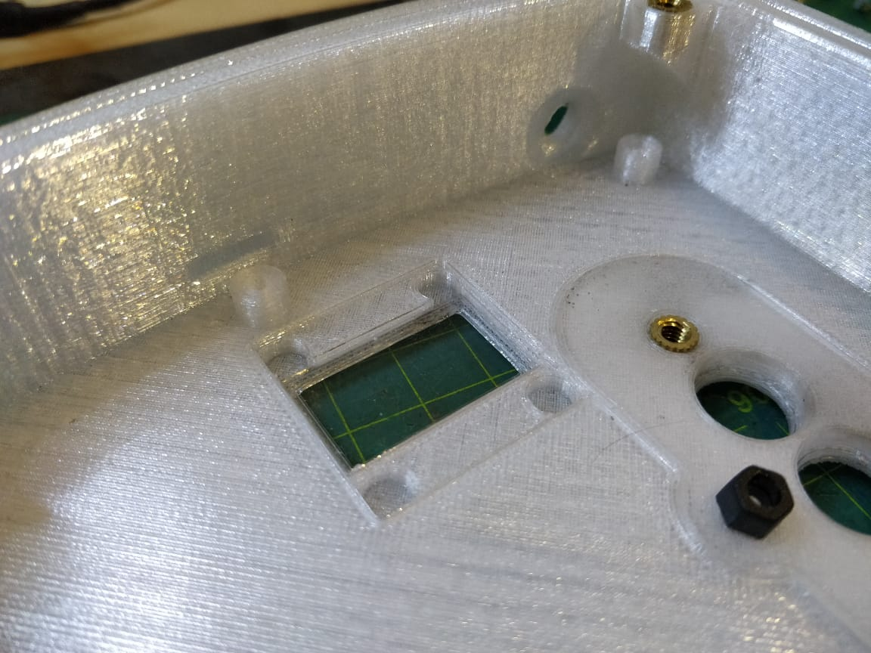
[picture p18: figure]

2. Align PCB corner with notch as indicated, and align SMA connector with SMA connector hole, and gently twist into position.

Ensure switch caps are properly aligned with the holes while twisting into place.

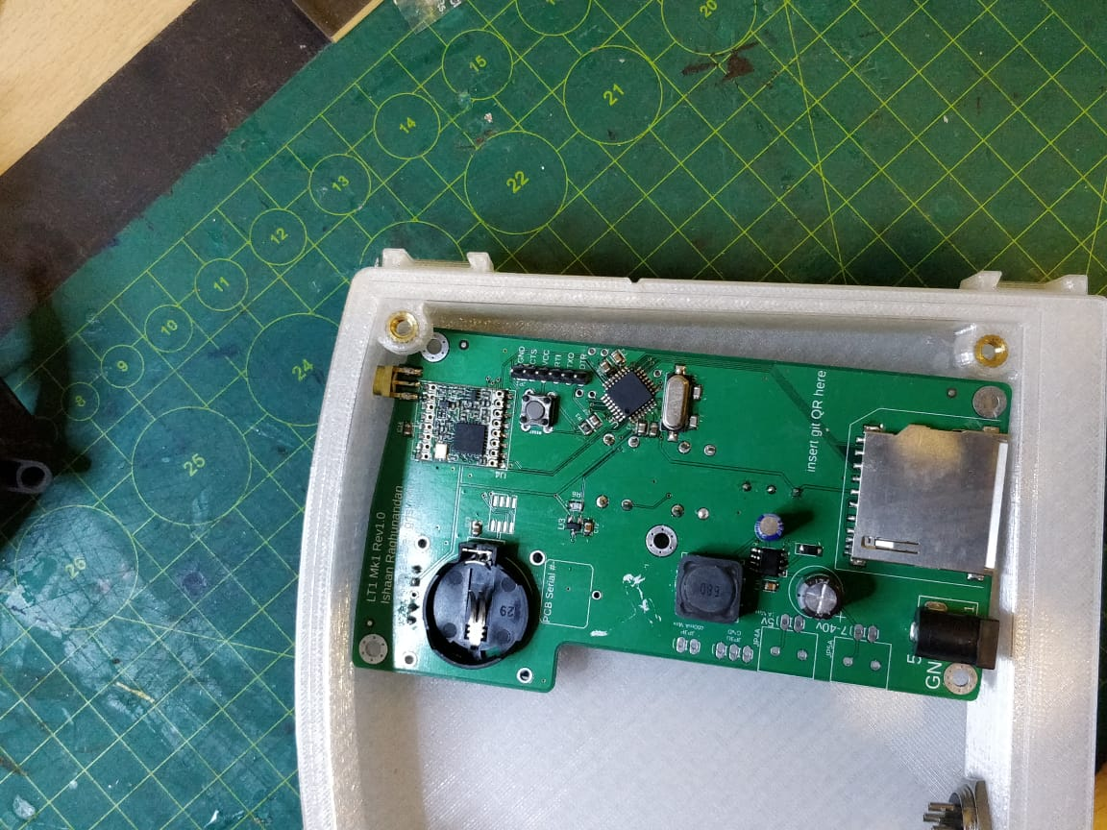
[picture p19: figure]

3. Use 4x M3x6 screw to secure PCB into place, and 1x M3x12mm screw in the centre.
4. Check that buttons can be pressed and the switch toggled.

# Acrylic Cover Assembly Order

1. Take 10 m4x15 bolts, slide rubber washers into place.
2. Take 3 A4 e-clips and use a pair of pliers to gently squeeze them tighter. Opening needs to reduce by about 1mm, but don't stress about it.
3. Take port and button covers, insert 3x prepped m4 bolts into place. Note port orientation
4. Use pliers to press 3x e-clips into place to retain the bolts.
5. Finally, Peel off acrylic protection.

# General guidelines

1. Apply a firm but gentle amount of torque while tightening the bolts. Overtightening will compromise the inserts or prints.
2. All M4 bolts can be used with a Rubber washer to increase water resistance, although care must be taken to prevent Rubber washer squeeze out. Ideally, 1mm rubber washers can be used instead, as they do not require any sealing fasteners.
3. Consider adding a dot of CA glue to the edges of the brass inserts once they are assembled, to gap-fill.
4. The 16mm Roundshell connectors can be further secured with a drop of superglue between the metal and plastic components. Care must be taken to avoid marring the threads.
5. Ensure all CA glue joints are properly ‘wetted’ during assembly, to prevent leaks.
6. Consider using a silicone sealant on main external joints, especially around the SMA connector’s port after the device is assembled and the antenna fixed to further reduce chances of water ingress.
7. The TPU/Silicone button and port plugs reduce the IP rating of the LBS, it is recommended to limit water exposure to droplets at most when the covers are in place, and keep it completely dry at all times.

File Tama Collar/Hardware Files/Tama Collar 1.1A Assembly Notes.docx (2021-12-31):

# Tama Collar 1.1A Assembly Notes

# Enclosure Shell Notes

1. Material- 2mm ABS 5”x5” sheets per shell
2. Machine- IDS Denmed Dental Vacuum Former
3. Forming bucks are machined from POM with silicone-based release spray.
4. A set of Dremel, tin snips, and flush cutters are used to cutout & clean the blanks.

# Assembly Order-

1. Prepare the PCB, Battery, Case shells and a 6” length of ball chain, and several magnets.
2. Use masking tape to secure a magnet to the reed switch, then solder the battery terminals to the PCB.
3. Tape another magnet over the upper shell to disable the reed switch, then insert the electronics into the upper shell. Peel away the first magnet when doing so.
4. Place the length of ball chain into the upper shell, ensuring it fits into the notches intended for it.
5. Close the lower shell over the upper shell, ensuring minimal gaps all around the seam.
6. Apply glue to seal the seams, avoid gluing the magnet or tape to the case while doing so.
7. Ensure disabling magnet is still firmly in place and pack the unit into it’s enclosure.

# Vacuum forming and Blank prep notes-

1. Ensure ABS is dehydrated prior to vacuum forming, minimum 12 hours at 60c.
2. Depending on whether the bucks are mounted to a backing board or not, it may help to use a screw to aid in extracting the buck from the pull. A gentle mist of silicone spray every 4 pulls is also recommended.
3. When cutting the case from the pull, ensure the edges are crisp but not sharp. Sand down sharp edges, and discard pulls with overly thin or translucent corners.
4. Once the case is cut from the pull, you will need to use a Dremel cutoff wheel (0.8-1mm thick) to cut two slots to allow the ballchain to sit inside the upper case.

## Exploded View

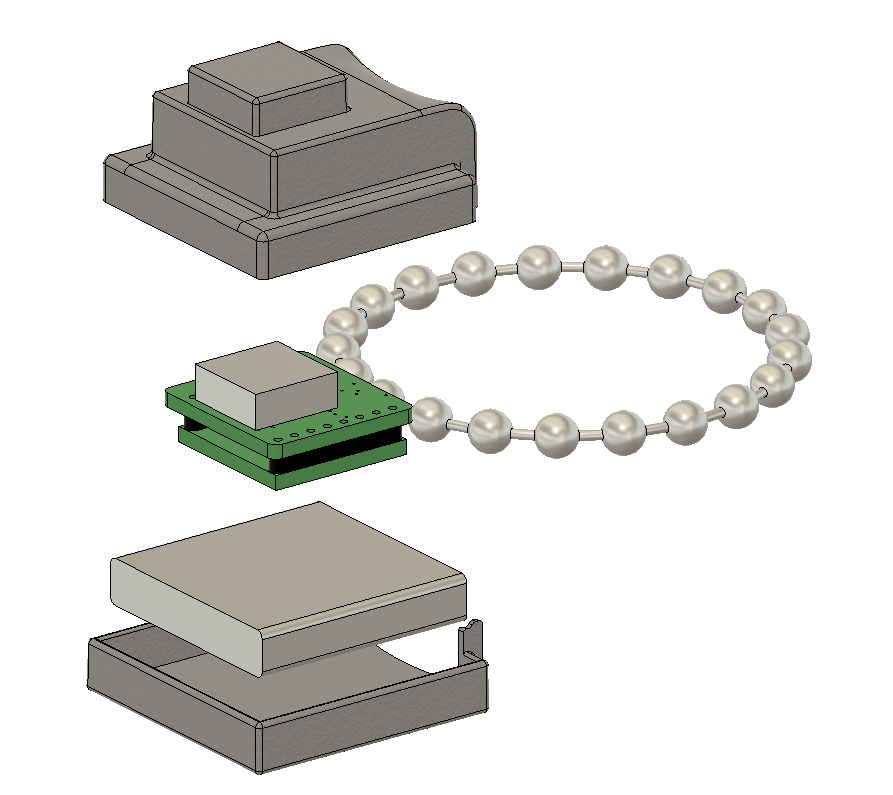
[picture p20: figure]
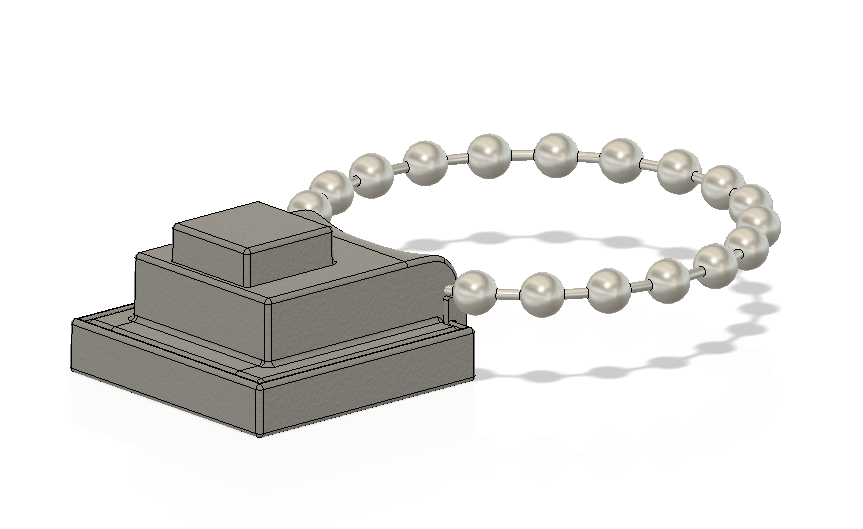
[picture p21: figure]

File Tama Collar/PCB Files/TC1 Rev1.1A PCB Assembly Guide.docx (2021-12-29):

# TC1 Rev1.1A Assembly Guide

TOP SIDE BOTTOM SIDE

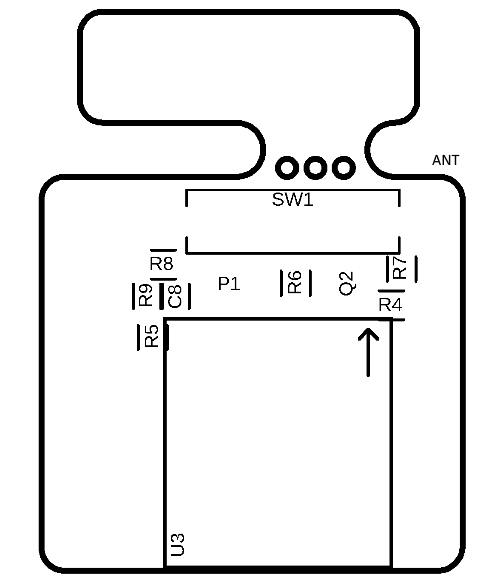
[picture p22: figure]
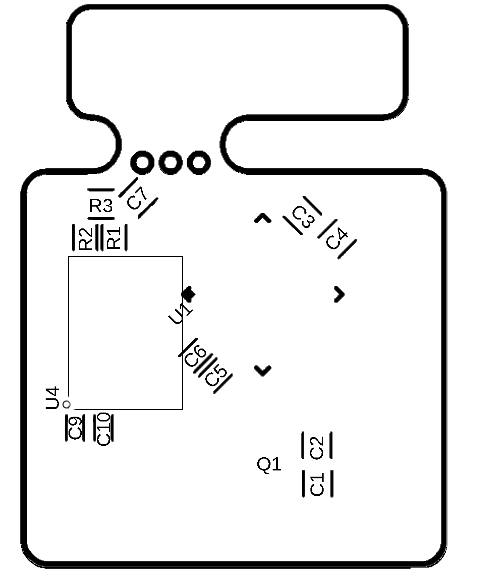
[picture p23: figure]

Qty | Value | Footprint | Package | Designator
7 | 0.1uF | C_CHIP-0402 | CAPC1005X60 | C3 to C7, C9, C10
8 | 10k | R_CHIP-0402 | RESC1005X40 | R1 to R8
0 | 10pF (DO NOT POPULATE) | C_CHIP-0402 | CAPC1005X60 | C1, C2
1 | 1uF | C_CHIP-0402 | CAPC1005X60 | C8
1 | 22k | R_CHIP-0402 | RESC1005X40 | R9
1 | 8mhz | CRYSTAL | CRYSTAL_NX3225GD | Q1
1 | ATMEGA328P-MU | ATMEGA328P-MU | QFN32_5X5_0.50 | U1
1 | DS3231MZ+ | DS3231MZ+ | DS3231MZ+_SOIC8 | U4
1 | GPS_ORG1411 | GPS_ORG1411 | ORG1411 | U3
1 | LDO_TPS7A0318DBVR | LDO_MIC5205YM5 | MIC5205 | P1
1 | NMOSFET | NMOSFETSOT23 | SOT23 | Q2
1 | REED_SWITCH | REED_SWITCH | REED_CT05 | SW1
1 | 26-28 SWG Jumper | Shown in Jumper Connections | | JU1

Notes-

- U3 pin 1 has a longer pad than the others. Pin 1 pad is near upwards pointing arrow on Top side.
- Please take steps to avoid short circuits with neighbouring pads, and to ensure that the correct pads are jumped as indicated in the above diagram. Jumpers to be installed last.

# Jumper Connections

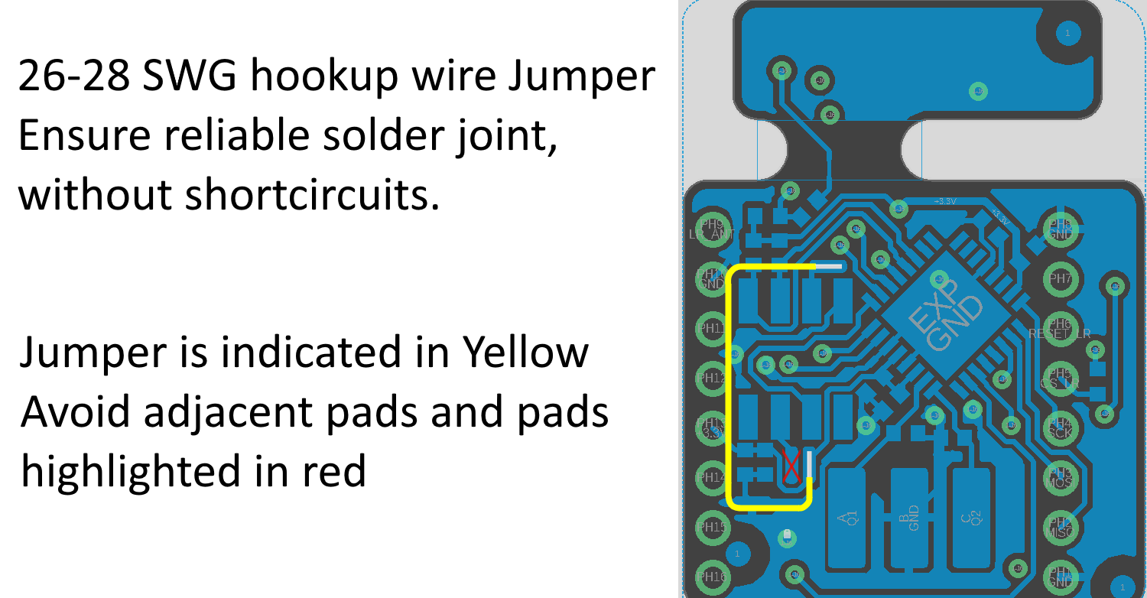
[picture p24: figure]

Number of Jumpers – 1

# Programming Pinouts

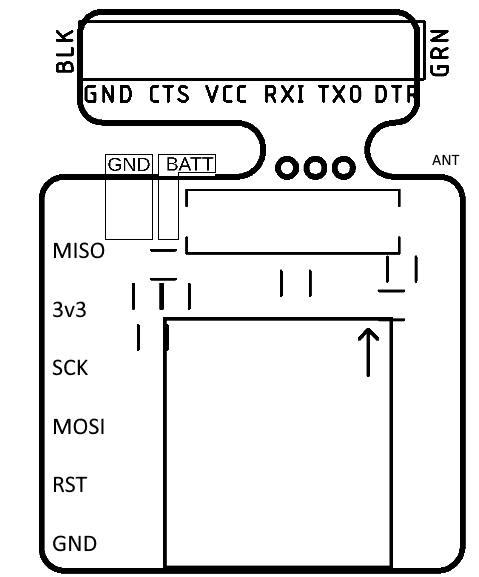
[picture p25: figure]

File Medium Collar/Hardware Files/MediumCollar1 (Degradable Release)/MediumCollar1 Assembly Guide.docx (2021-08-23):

# MediumCollar1 Assembly Guide

# Parts list

1. Type C Case x1
2. Type C Lid x1
3. MC1 PCB x1
4. LS14500 Battery x1
5. Magnet x1
6. Plastite Screws CSK x5
7. Loctite SL 596
8. IPA/degreasing solvent

Note on Loctite SL596-

The sealant cures on exposure to atmospheric moisture, and can cure up to 6mm thick. It’s best applied in a thin, uniform and continuous bead around 1mm thick in dia.

# Assembly steps-

1. Ensure part quality- Check for any loose strands of plastic, debris, cracks or irregularities in 3D printed parts.
2. Tape magnet into place at the far end of the case to disconnect the battery reed switch once the electronics have been inserted into the case.
3. Solder battery connections- Solder the battery connections to the MC1 PCB and ensure antenna wire is soldered firmly.
4. Ensure fit- Slide MC1 & Battery into the case. Fit should be snug with a little wiggle room. EVA foam or folded cardboard can be used to stop rattling.

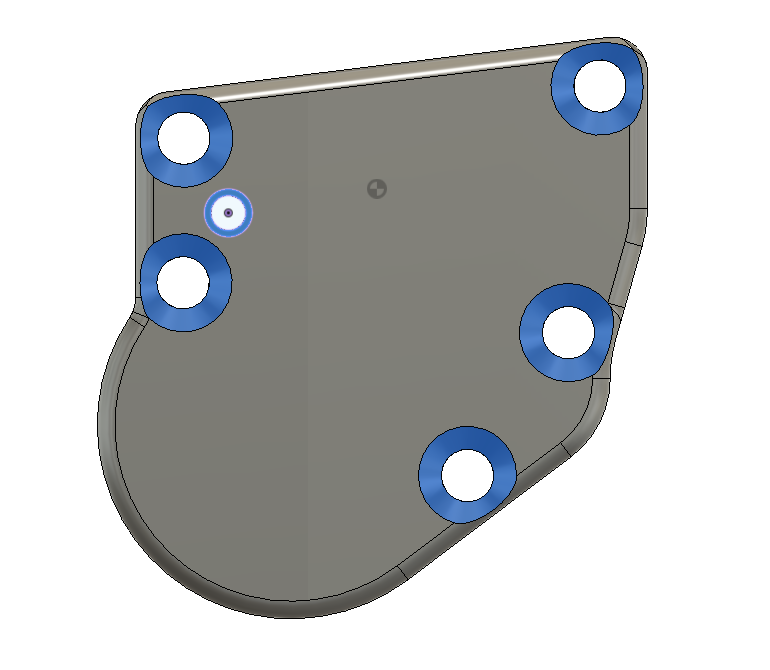
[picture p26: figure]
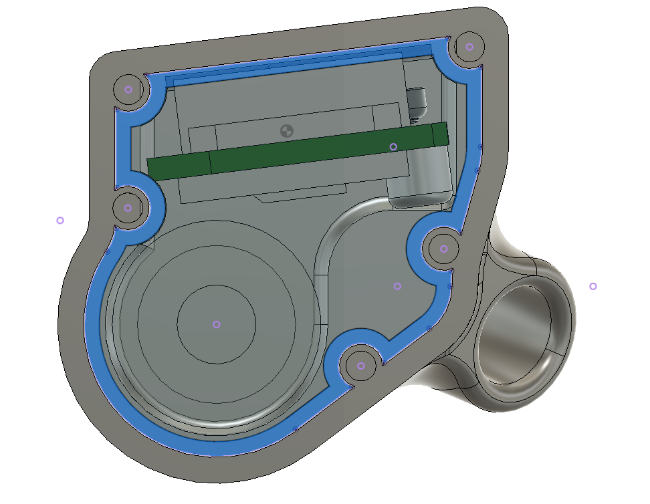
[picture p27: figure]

5. Clean gasket surfaces of both 3D printed parts with IPA to ensure a tight seal. Let dry.

Sealing gasket surface highlighted in blue

6. Apply a thin, uniform and continuous bead of silicone sealant to the gasket surface on the Case side.
7. Insert antenna wire through its hole until there is ½ inch of space before closing the case, and apply a thin bead of silicone sealant around the base.

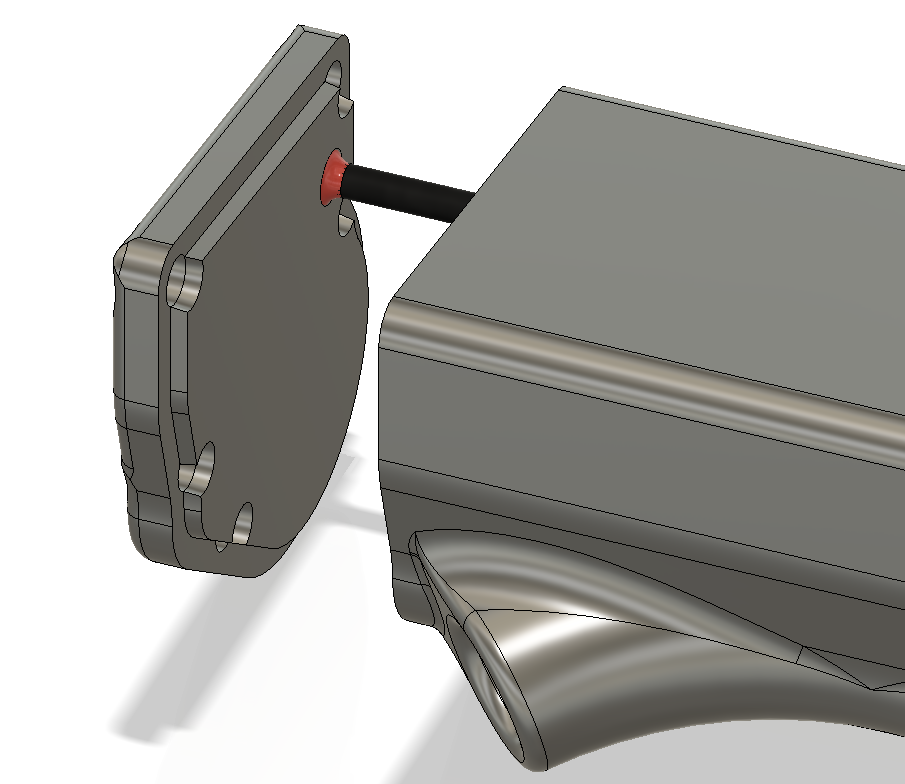
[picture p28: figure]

Sealant here is highlighted in Red around the antenna wire

8. Close the case gently, and apply additional silicone sealant around the antenna wire. Wipe away excess sealant.
9. Apply a thin layer of silicone sealant around the screw holes as highlighted in Step 5.
10. Insert 5 plastite screws and uniformly tighten them. Overtightening could lead to stripped screw bosses.
11. Wipe away any silicone sealant that oozed out from the screw holes or sealing flange.

The device should now be ready for dispatch.

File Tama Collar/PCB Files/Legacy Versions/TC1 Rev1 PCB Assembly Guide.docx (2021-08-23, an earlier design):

# TC1 Rev1 Assembly Guide

TOP SIDE BOTTOM SIDE


Qty | Value | Footprint | Package | Designator
7 | 0.1uF | C_CHIP-0402 | CAPC1005X60 | C3 to C7, C9, C10
8 | 10k | R_CHIP-0402 | RESC1005X40 | R1 to R8
2 | 10pF | C_CHIP-0402 | CAPC1005X60 | C1, C2
1 | 1uF | C_CHIP-0402 | CAPC1005X60 | C8
1 | 22k | R_CHIP-0402 | RESC1005X40 | R9
1 | 8mhz | CRYSTAL | CRYSTAL_NX3225GD | Q1
1 | ATMEGA328P-MU | ATMEGA328P-MU | QFN32_5X5_0.50 | U1
1 | DS3231MZ+ | DS3231MZ+ | DS3231MZ+_SOIC8 | U4
1 | GPS_ORG1411 | GPS_ORG1411 | ORG1411 | U3
1 | LDO_MIC5205YM5 | LDO_MIC5205YM5 | MIC5205 | P1
1 | NMOSFET | NMOSFETSOT23 | SOT23 | Q2
1 | REED_SWITCH | REED_SWITCH | REED_CT05 | SW1

Notes-

- U3 pin 1 has a longer pad than the others. Pin 1 pad is near upwards pointing arrow on Top side.

# Programming Pinouts


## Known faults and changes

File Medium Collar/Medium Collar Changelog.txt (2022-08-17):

### Medium Collar Changelog
#### Release 1
- Initial Release

#### PCB Revision 1.1 
- Completely overhauled PCB
- Swapped GPS PA6H for GPS L80-M39
- Added motor control
- Added EEPROM 24LC512

#### Hardware Revision 1.1 
- Added motorized release mechanism

#### PCB Revision 1.2
- Added Resistors to limit inrush current on GPS & Motor Mosfet.
- Changed DS3231MZ power to Vbat instead of VCC to improve current consumption.

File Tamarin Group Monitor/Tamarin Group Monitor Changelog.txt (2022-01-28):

### Tamarin Group Monitor Changelog
#### Release 1
- Initial Release

#### PCB Revision 1.1 
To Do
Change Screw layout on camera module to 4 screws from 3. 35mm apart

Add keepout around ESP32 antenna
Rotate the PIR sensor upsidedown.
Add options for relays/mosfets for Illuminator control.

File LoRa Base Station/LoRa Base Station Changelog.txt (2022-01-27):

### LoRa Base Station Changelog
#### Release 1
- Initial Release

#### PCB Revision 1.1
- Added USB port for charging devices
- Changed both ports to USB-C

#### PCB Revision 1.2
- Changed MCU to ESP32
- Changed GPS to L80-M39

#### Hardware Revision 1.2
//Synchronized PCB Revision and case revision to avoid confusion.
- Swapped EPDM Rubber O-Rings for Rubber Washers(nitrile)
- Swapped TPU plugs for RTV Silicone cast plugs

#### PCB Revision 1.3
- Added Resistor to limit inrush current on GPS Mosfet.
- Fixed RTC crystal footprint
- Fixed UART lines
- Pin change- GPSPower to IO35?

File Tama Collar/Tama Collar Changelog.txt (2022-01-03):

### Tama Collar Changelog
#### Release 1
- Initial Release

#### PCB Revision 1.1
- Swapped LDO to TPS7A0318DBVR
- Disconnected RTC VCC and added pads for manual power jumpering

#### PCB Revision 1.1A
- Removed mousebites on breakaway FTDI headers on request from PCB fabricator.

#### PCB Revision 1.2 (unreleased)
- Moved Name silks to a better spot to avoid overlap with fiducials
- Corrected assembly error involving resonator caps?
- Solar Power?

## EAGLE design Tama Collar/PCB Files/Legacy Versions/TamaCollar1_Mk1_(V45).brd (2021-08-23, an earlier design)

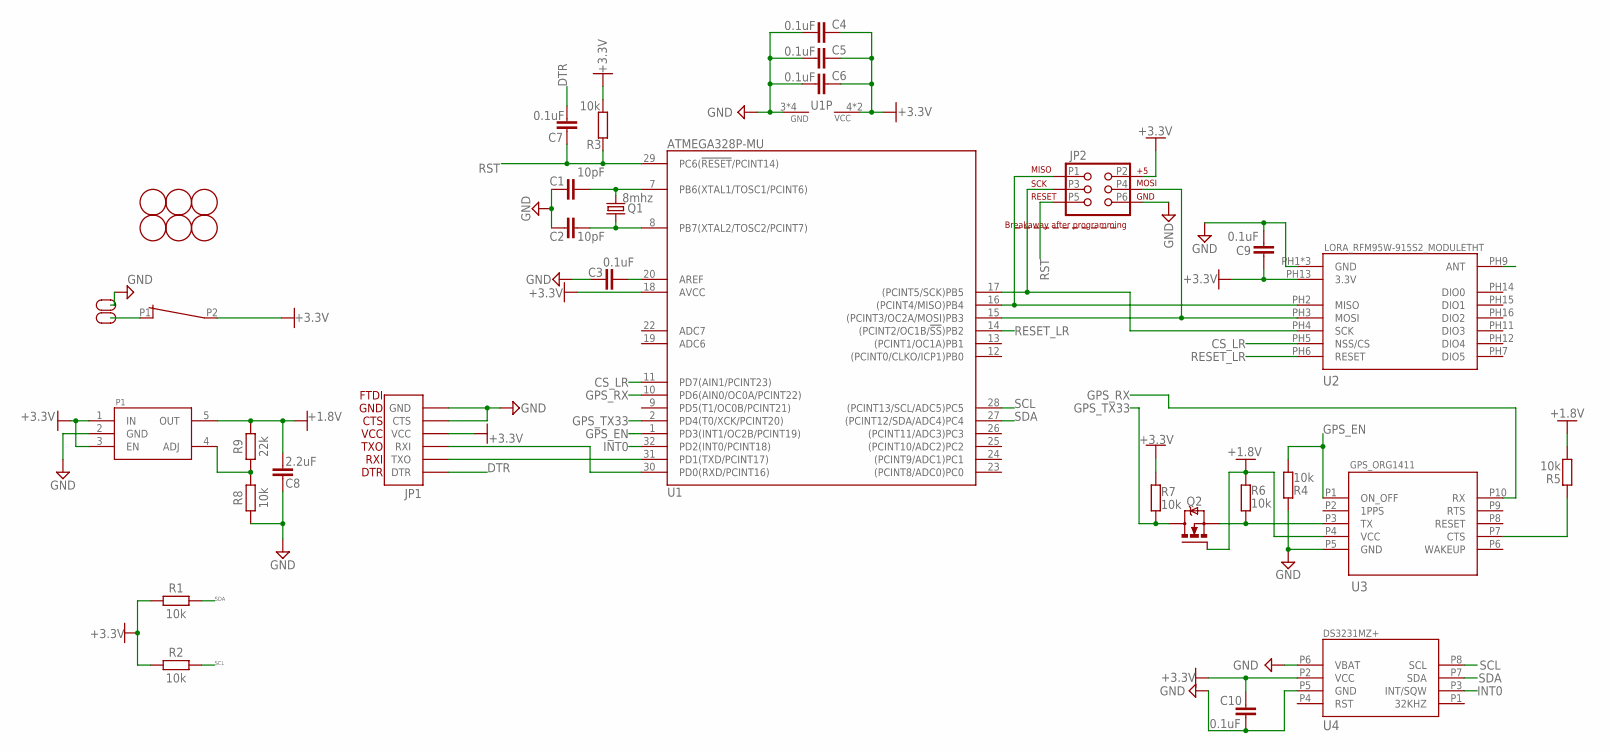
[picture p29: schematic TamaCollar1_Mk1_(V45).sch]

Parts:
BATT+: BREAKOUT_PADL; BREAKOUT_PAD*1*1X2MM
BR2: MOUSEBITE3X1.25; MOUSEBITE_3H_6TRACE(1.25MM)
C1, C2: 10pF; CAPC1005X60
C3, C4, C5, C6, C7, C9, C10: 0.1uF; CAPC1005X60
C8: 2.2uF; CAPC1005X60
F1, F2, F3, F4, F5, F6: FIDUCIAL; FIDUCIAL_1MM
GND: BREAKOUT_PADL; BREAKOUT_PAD*1*1X2MM
JP1: FTDI_DEVICESMALL; FTDI_DEVICE_SMD_SMALL
JP2: AVR_SPI_PRG_61X6; 1X6-SMD
P1: LDO_MIC5205YM5; MIC5205
Q1: 8mhz; CRYSTAL_NX3225GD
Q2: NMOSFET; SOT23
R1, R2, R3, R4, R5, R6, R7, R8: 10k; RESC1005X40
R9: 22k; RESC1005X40
SW1: REED_SWITCH; REED_CT05
U1: ATMEGA328P-MU; QFN32_5X5_0.50
U2: LORA_RFM95W-915S2_MODULETHT; LORA_RFM95W-915S2_16STANDOFFMODULE
U3: GPS_ORG1411; ORG1411
U4: DS3231MZ+; DS3231MZ+_SOIC8

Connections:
+1.8V: C8.2, P1.5 (OUT), Q2.1 (G), R5.1, R6.2, R9.2, U3.P4 (VCC)
+3.3V: C4.1, C5.1, C6.1, C9.1, C10.1, JP1.P4 (VCC), JP2.P2 (2), P1.1 (IN), P1.3 (EN), R1.1, R2.1, R3.1, R7.2, SW1.P2 (PAD2), U1.4 (VCC), U1.6 (VCC), U1.18 (AVCC), U2.PH13 (3.3V), U4.P2 (VCC)
+BATT: BATT+.P$1, SW1.P1 (PAD1)
AREF: C3.2, U1.20 (AREF)
CS_LR: U1.11 (PD7(AIN1/PCINT23)), U2.PH5 (NSS/CS)
DTR: C7.2, JP1.P1 (DTR)
GND: C1.1, C2.1, C3.1, C4.2, C5.2, C6.2, C8.1, C9.2, C10.2, GND.P$1, JP1.P5 (CTS), JP1.P6 (GND), JP2.P6 (6), P1.2 (GND), R4.2, R8.1, U1.3 (GND), U1.5 (GND), U1.21 (GND), U1.EXP (GND), U2.PH1 (GND), U2.PH8 (GND), U2.PH10 (GND), U3.P5 (GND), U4.P5 (GND), U4.P6 (VBAT)
GPS_CTS: R5.2, U3.P7 (CTS)
GPS_EN: R4.1, U1.1 (PD3(INT1/OC2B/PCINT19)), U3.P1 (ON_OFF)
GPS_RX: U1.10 (PD6(AIN0/OC0A/PCINT22)), U3.P10 (RX)
GPS_TX18: Q2.2 (S), R6.1, U3.P3 (TX)
GPS_TX33: Q2.3 (D), R7.1, U1.2 (PD4(T0/XCK/PCINT20))
INT0: U1.32 (PD2(INT0/PCINT18)), U4.P3 (INT/SQW)
LR_ANT: U2.PH9 (ANT)
MISO: JP2.P1 (1), U1.16 ((PCINT4/MISO)PB4), U2.PH2 (MISO)
MOSI: JP2.P4 (4), U1.15 ((PCINT3/OC2A/MOSI)PB3), U2.PH3 (MOSI)
P1ADJ: P1.4 (ADJ), R8.2, R9.1
Q1: C1.2, Q1.P2 (2), U1.7 (PB6(XTAL1/TOSC1/PCINT6))
Q2: C2.2, Q1.P1 (1), U1.8 (PB7(XTAL2/TOSC2/PCINT7))
RESET_LR: U1.14 ((PCINT2/OC1B/!SS!)PB2), U2.PH6 (RESET)
RST: C7.1, JP2.P5 (5), R3.2, U1.29 (PC6(!RESET!/PCINT14))
RXD: JP1.P3 (RXI), U1.30 (PD0(RXD/PCINT16))
SCK: JP2.P3 (3), U1.17 ((PCINT5/SCK)PB5), U2.PH4 (SCK)
SCL: R2.2, U1.28 ((PCINT13/SCL/ADC5)PC5), U4.P8 (SCL)
SDA: R1.2, U1.27 ((PCINT12/SDA/ADC4)PC4), U4.P7 (SDA)
TXD: JP1.P2 (TXO), U1.31 (PD1(TXD/PCINT17))

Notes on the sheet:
FTDI GND CTS VCC TXO RXI DTR

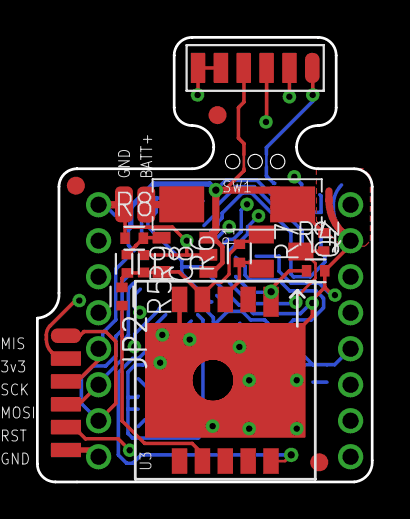
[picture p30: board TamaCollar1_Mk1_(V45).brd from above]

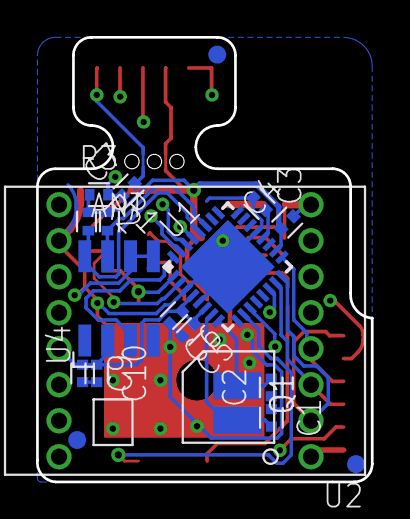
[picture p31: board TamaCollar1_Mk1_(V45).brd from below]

Board: 4 copper layers, 18.6 x 24.7 mm, 38 parts (19 on the bottom side), 25 nets.

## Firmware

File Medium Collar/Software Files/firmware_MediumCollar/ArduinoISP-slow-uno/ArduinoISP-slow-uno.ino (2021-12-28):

// ArduinoISP
// Copyright (c) 2008-2011 Randall Bohn
// If you require a license, see
// http://www.opensource.org/licenses/bsd-license.php
//
// This sketch turns the Arduino into a AVRISP using the following Arduino pins:
//
// Pin 10 is used to reset the target microcontroller.
//
// By default, the hardware SPI pins MISO, MOSI and SCK are used to communicate
// with the target. On all Arduinos, these pins can be found
// on the ICSP/SPI header:
//
//               MISO °. . 5V (!) Avoid this pin on Due, Zero...
//               SCK   . . MOSI
//                     . . GND
//
// On some Arduinos (Uno,...), pins MOSI, MISO and SCK are the same pins as
// digital pin 11, 12 and 13, respectively. That is why many tutorials instruct
// you to hook up the target to these pins. If you find this wiring more
// practical, have a define USE_OLD_STYLE_WIRING. This will work even when not
// using an Uno. (On an Uno this is not needed).
//
// Alternatively you can use any other digital pin by configuring
// software ('BitBanged') SPI and having appropriate defines for PIN_MOSI,
// PIN_MISO and PIN_SCK.
//
// IMPORTANT: When using an Arduino that is not 5V tolerant (Due, Zero, ...) as
// the programmer, make sure to not expose any of the programmer's pins to 5V.
// A simple way to accomplish this is to power the complete system (programmer
// and target) at 3V3.
//
// Put an LED (with resistor) on the following pins:
// 9: Heartbeat   - shows the programmer is running
// 8: Error       - Lights up if something goes wrong (use red if that makes sense)
// 7: Programming - In communication with the slave
//

#include "Arduino.h"
#undef SERIAL


#define PROG_FLICKER true

// Configure SPI clock (in Hz).
// E.g. for an ATtiny @ 128 kHz: the datasheet states that both the high and low
// SPI clock pulse must be > 2 CPU cycles, so take 3 cycles i.e. divide target
// f_cpu by 6:
//     #define SPI_CLOCK            (128000/6)
//
// A clock slow enough for an ATtiny85 @ 1 MHz, is a reasonable default:

#define SPI_CLOCK 		(128000/6)


// Select hardware or software SPI, depending on SPI clock.
// Currently only for AVR, for other architectures (Due, Zero,...), hardware SPI
// is probably too fast anyway.

#if defined(ARDUINO_ARCH_AVR)

#if SPI_CLOCK > (F_CPU / 128)
#define USE_HARDWARE_SPI
#endif

#endif

// Configure which pins to use:

// The standard pin configuration.
#ifndef ARDUINO_HOODLOADER2

#define RESET     10 // Use pin 10 to reset the target rather than SS
#define LED_HB    9
#define LED_ERR   8
#define LED_PMODE 7

// Uncomment following line to use the old Uno style wiring
// (using pin 11, 12 and 13 instead of the SPI header) on Leonardo, Due...

// #define USE_OLD_STYLE_WIRING

#ifdef USE_OLD_STYLE_WIRING

#define PIN_MOSI	11
#define PIN_MISO	12
#define PIN_SCK		13

#endif

// HOODLOADER2 means running sketches on the ATmega16U2 serial converter chips
// on Uno or Mega boards. We must use pins that are broken out:
#else

#define RESET     	4
#define LED_HB    	7
#define LED_ERR   	6
#define LED_PMODE 	5

#endif

// By default, use hardware SPI pins:
#ifndef PIN_MOSI
#define PIN_MOSI 	MOSI
#endif

#ifndef PIN_MISO
#define PIN_MISO 	MISO
#endif

#ifndef PIN_SCK
#define PIN_SCK 	SCK
#endif

// Force bitbanged SPI if not using the hardware SPI pins:
#if (PIN_MISO != MISO) ||  (PIN_MOSI != MOSI) || (PIN_SCK != SCK)
#undef USE_HARDWARE_SPI
#endif


// Configure the serial port to use.
//
// Prefer the USB virtual serial port (aka. native USB port), if the Arduino has one:
//   - it does not autoreset (except for the magic baud rate of 1200).
//   - it is more reliable because of USB handshaking.
//
// Leonardo and similar have an USB virtual serial port: 'Serial'.
// Due and Zero have an USB virtual serial port: 'SerialUSB'.
//
// On the Due and Zero, 'Serial' can be used too, provided you disable autoreset.
// To use 'Serial': #define SERIAL Serial

#ifdef SERIAL_PORT_USBVIRTUAL
#define SERIAL SERIAL_PORT_USBVIRTUAL
#else
#define SERIAL Serial
#endif


// Configure the baud rate:

#define BAUDRATE	19200
// #define BAUDRATE	115200
// #define BAUDRATE	1000000


#define HWVER 2
#define SWMAJ 1
#define SWMIN 18

// STK Definitions
#define STK_OK      0x10
#define STK_FAILED  0x11
#define STK_UNKNOWN 0x12
#define STK_INSYNC  0x14
#define STK_NOSYNC  0x15
#define CRC_EOP     0x20 //ok it is a space...

void pulse(int pin, int times);

#ifdef USE_HARDWARE_SPI
#include "SPI.h"
#else

#define SPI_MODE0 0x00

class SPISettings {
  public:
    // clock is in Hz
    SPISettings(uint32_t clock, uint8_t bitOrder, uint8_t dataMode) : clock(clock) {
      (void) bitOrder;
      (void) dataMode;
    };

  private:
    uint32_t clock;

    friend class BitBangedSPI;
};

class BitBangedSPI {
  public:
    void begin() {
      digitalWrite(PIN_SCK, LOW);
      digitalWrite(PIN_MOSI, LOW);
      pinMode(PIN_SCK, OUTPUT);
      pinMode(PIN_MOSI, OUTPUT);
      pinMode(PIN_MISO, INPUT);
    }

    void beginTransaction(SPISettings settings) {
      pulseWidth = (500000 + settings.clock - 1) / settings.clock;
      if (pulseWidth == 0)
        pulseWidth = 1;
    }

    void end() {}

    uint8_t transfer (uint8_t b) {
      for (unsigned int i = 0; i < 8; ++i) {
        digitalWrite(PIN_MOSI, (b & 0x80) ? HIGH : LOW);
        digitalWrite(PIN_SCK, HIGH);
        delayMicroseconds(pulseWidth);
        b = (b << 1) | digitalRead(PIN_MISO);
        digitalWrite(PIN_SCK, LOW); // slow pulse
        delayMicroseconds(pulseWidth);
      }
      return b;
    }

  private:
    unsigned long pulseWidth; // in microseconds
};

static BitBangedSPI SPI;

#endif

void setup() {
  SERIAL.begin(BAUDRATE);

  pinMode(LED_PMODE, OUTPUT);
  pulse(LED_PMODE, 2);
  pinMode(LED_ERR, OUTPUT);
  pulse(LED_ERR, 2);
  pinMode(LED_HB, OUTPUT);
  pulse(LED_HB, 2);

}

int error = 0;
int pmode = 0;
// address for reading and writing, set by 'U' command
unsigned int here;
uint8_t buff[256]; // global block storage

#define beget16(addr) (*addr * 256 + *(addr+1) )
typedef struct param {
  uint8_t devicecode;
  uint8_t revision;
  uint8_t progtype;
  uint8_t parmode;
  uint8_t polling;
  uint8_t selftimed;
  uint8_t lockbytes;
  uint8_t fusebytes;
  uint8_t flashpoll;
  uint16_t eeprompoll;
  uint16_t pagesize;
  uint16_t eepromsize;
  uint32_t flashsize;
}
parameter;

parameter param;

// this provides a heartbeat on pin 9, so you can tell the software is running.
uint8_t hbval = 128;
int8_t hbdelta = 8;
void heartbeat() {
  static unsigned long last_time = 0;
  unsigned long now = millis();
  if ((now - last_time) < 40)
    return;
  last_time = now;
  if (hbval > 192) hbdelta = -hbdelta;
  if (hbval < 32) hbdelta = -hbdelta;
  hbval += hbdelta;
  analogWrite(LED_HB, hbval);
}

static bool rst_active_high;

void reset_target(bool reset) {
  digitalWrite(RESET, ((reset && rst_active_high) || (!reset && !rst_active_high)) ? HIGH : LOW);
}

void loop(void) {
  // is pmode active?
  if (pmode) {
    digitalWrite(LED_PMODE, HIGH);
  } else {
    digitalWrite(LED_PMODE, LOW);
  }
  // is there an error?
  if (error) {
    digitalWrite(LED_ERR, HIGH);
  } else {
    digitalWrite(LED_ERR, LOW);
  }

  // light the heartbeat LED
  heartbeat();
  if (SERIAL.available()) {
    avrisp();
  }
}

uint8_t getch() {
  while (!SERIAL.available());
  return SERIAL.read();
}
void fill(int n) {
  for (int x = 0; x < n; x++) {
    buff[x] = getch();
  }
}

#define PTIME 30
void pulse(int pin, int times) {
  do {
    digitalWrite(pin, HIGH);
    delay(PTIME);
    digitalWrite(pin, LOW);
    delay(PTIME);
  } while (times--);
}

void prog_lamp(int state) {
  if (PROG_FLICKER) {
    digitalWrite(LED_PMODE, state);
  }
}

uint8_t spi_transaction(uint8_t a, uint8_t b, uint8_t c, uint8_t d) {
  SPI.transfer(a);
  SPI.transfer(b);
  SPI.transfer(c);
  return SPI.transfer(d);
}

void empty_reply() {
  if (CRC_EOP == getch()) {
    SERIAL.print((char)STK_INSYNC);
    SERIAL.print((char)STK_OK);
  } else {
    error++;
    SERIAL.print((char)STK_NOSYNC);
  }
}

void breply(uint8_t b) {
  if (CRC_EOP == getch()) {
    SERIAL.print((char)STK_INSYNC);
    SERIAL.print((char)b);
    SERIAL.print((char)STK_OK);
  } else {
    error++;
    SERIAL.print((char)STK_NOSYNC);
  }
}

void get_version(uint8_t c) {
  switch (c) {
    case 0x80:
      breply(HWVER);
      break;
    case 0x81:
      breply(SWMAJ);
      break;
    case 0x82:
      breply(SWMIN);
      break;
    case 0x93:
      breply('S'); // serial programmer
      break;
    default:
      breply(0);
  }
}

void set_parameters() {
  // call this after reading parameter packet into buff[]
  param.devicecode = buff[0];
  param.revision   = buff[1];
  param.progtype   = buff[2];
  param.parmode    = buff[3];
  param.polling    = buff[4];
  param.selftimed  = buff[5];
  param.lockbytes  = buff[6];
  param.fusebytes  = buff[7];
  param.flashpoll  = buff[8];
  // ignore buff[9] (= buff[8])
  // following are 16 bits (big endian)
  param.eeprompoll = beget16(&buff[10]);
  param.pagesize   = beget16(&buff[12]);
  param.eepromsize = beget16(&buff[14]);

  // 32 bits flashsize (big endian)
  param.flashsize = buff[16] * 0x01000000
                    + buff[17] * 0x00010000
                    + buff[18] * 0x00000100
                    + buff[19];

  // AVR devices have active low reset, AT89Sx are active high
  rst_active_high = (param.devicecode >= 0xe0);
}

void start_pmode() {

  // Reset target before driving PIN_SCK or PIN_MOSI

  // SPI.begin() will configure SS as output, so SPI master mode is selected.
  // We have defined RESET as pin 10, which for many Arduinos is not the SS pin.
  // So we have to configure RESET as output here,
  // (reset_target() first sets the correct level)
  reset_target(true);
  pinMode(RESET, OUTPUT);
  SPI.begin();
  SPI.beginTransaction(SPISettings(SPI_CLOCK, MSBFIRST, SPI_MODE0));

  // See AVR datasheets, chapter "SERIAL_PRG Programming Algorithm":

  // Pulse RESET after PIN_SCK is low:
  digitalWrite(PIN_SCK, LOW);
  delay(20); // discharge PIN_SCK, value arbitrarily chosen
  reset_target(false);
  // Pulse must be minimum 2 target CPU clock cycles so 100 usec is ok for CPU
  // speeds above 20 KHz
  delayMicroseconds(100);
  reset_target(true);

  // Send the enable programming command:
  delay(50); // datasheet: must be > 20 msec
  spi_transaction(0xAC, 0x53, 0x00, 0x00);
  pmode = 1;
}

void end_pmode() {
  SPI.end();
  // We're about to take the target out of reset so configure SPI pins as input
  pinMode(PIN_MOSI, INPUT);
  pinMode(PIN_SCK, INPUT);
  reset_target(false);
  pinMode(RESET, INPUT);
  pmode = 0;
}

void universal() {
  uint8_t ch;

  fill(4);
  ch = spi_transaction(buff[0], buff[1], buff[2], buff[3]);
  breply(ch);
}

void flash(uint8_t hilo, unsigned int addr, uint8_t data) {
  spi_transaction(0x40 + 8 * hilo,
                  addr >> 8 & 0xFF,
                  addr & 0xFF,
                  data);
}
void commit(unsigned int addr) {
  if (PROG_FLICKER) {
    prog_lamp(LOW);
  }
  spi_transaction(0x4C, (addr >> 8) & 0xFF, addr & 0xFF, 0);
  if (PROG_FLICKER) {
    delay(PTIME);
    prog_lamp(HIGH);
  }
}

unsigned int current_page() {
  if (param.pagesize == 32) {
    return here & 0xFFFFFFF0;
  }
  if (param.pagesize == 64) {
    return here & 0xFFFFFFE0;
  }
  if (param.pagesize == 128) {
    return here & 0xFFFFFFC0;
  }
  if (param.pagesize == 256) {
    return here & 0xFFFFFF80;
  }
  return here;
}


void write_flash(int length) {
  fill(length);
  if (CRC_EOP == getch()) {
    SERIAL.print((char) STK_INSYNC);
    SERIAL.print((char) write_flash_pages(length));
  } else {
    error++;
    SERIAL.print((char) STK_NOSYNC);
  }
}
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

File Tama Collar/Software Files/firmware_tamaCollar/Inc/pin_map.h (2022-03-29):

#ifndef __PIN_MAP_H
#define __PIN_MAP_H

/* GPS Pins Mapping */
#ifndef MEDIUM_COLLAR
#define GPS_ON_OFF_PULSE_PORT       'D'
#define GPS_ON_OFF_PULSE_PIN       	3
#define	LORA_SS_PORT				'D'
#define LORA_SS_PIN					7
#define	LORA_RST_PORT				'B'
#define LORA_RST_PIN				2
#define SOFTUART_BAUD_RATE      	4800

// Soft UART Related stuff
#define SOFTUART_RXPIN   PIND
#define SOFTUART_RXDDR   DDRD
#define SOFTUART_RXBIT   PD4

#define SOFTUART_TXPORT  PORTD
#define SOFTUART_TXDDR   DDRD
#define SOFTUART_TXBIT   PD6
#endif

#ifdef MEDIUM_COLLAR
#define GPS_ON_OFF_PULSE_PORT       'D'
#define GPS_ON_OFF_PULSE_PIN       	4
#define	LORA_SS_PORT				'C'
#define LORA_SS_PIN					0
#define	LORA_RST_PORT				'C'
#define LORA_RST_PIN				1
#define SOFTUART_BAUD_RATE      	9600

// Motor Section
#define MOTOR_PWR_PORT				'D'
#define MOTOR_PWR_PIN				7
#define MOTOR_IN2_PORT				'D'
#define MOTOR_IN2_PIN				6
#define MOTOR_IN1_PORT				'D'
#define MOTOR_IN1_PIN				5

// Soft UART Related stuff
#define SOFTUART_RXPIN   PINB
#define SOFTUART_RXDDR   DDRB
#define SOFTUART_RXBIT   PB1

#define SOFTUART_TXPORT  PORTB
#define SOFTUART_TXDDR   DDRB
#define SOFTUART_TXBIT   PB0
#endif

#endif

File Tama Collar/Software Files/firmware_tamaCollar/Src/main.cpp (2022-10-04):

#include "main.h"
#include "pin_map.h"
#include "common.h"
#include "LoRa.h"
#include "spi.h"
#include "softuart_avr.h"
#include "TinyGPS++.h"
#include "scheduling.h"
#include <string.h>
#include "rtc.h"
#include "twi-lowlevel.h"
#include "command_layer.h"
#include "battery.h"
#include "eeprom_hal.h"
#ifdef MEDIUM_COLLAR
#include "medium_collar.h"
#include "ext_mem_eeprom.h"
#endif

// Global Variable
static CmdUARTInterface pkt_main;
static long timer_count = 0;
SchedulingManage schedule;
static char sen_pkt_buff [50];
bool rtc_time_set_flag = false;
static CmdProcess cmd;
uint8_t dev_id;

// GPS Pasrser setup
static TinyGPSPlus gps;

// Temp Debugging related functions
void displayInfo ();

/**
 * @brief ISR scanner
 * @details It's been called in Main loop continuously. It keep reading ISR BUffer and detects the given strings patterns
 */
void CmdUARTInterface::packetDetect (char source)
{
	while (this->isr_in != this->isr_out)
	{
		/*printf ("\r\nisr_in : %d, isr_out : %d : %c   Timer Count : %lu",
				this->isr_in, this->isr_out, this->isr_buff[this->isr_out], 
				this->_timer_count);*/
		switch (this->_packet_state)
		{
		case PKT_WAIT_SOH:
			if (this->isr_buff[this->isr_out] == PKT_SOH) // Waiting for start of packet
			{
				this->_packet_state = PKT_WAIT_EOH;
				//cmd.start_storing (this->isr_buff[this->isr_out]);
				this->_timer_count = PKT_TIMEOUT;
				////////printf ("\r\ncmd.packetDetect -> Detect Start of Header");
			}
			break;
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

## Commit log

2021-08-23 Added base files
    [Acrylic 2mm Window.dxf, Acrylic 5mm Button Cover.dxf, Acrylic 5mm Ports Cover.dxf, Acrylic 6mm Backplate.dxf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]
2021-12-16 adds the firmware for TamaCollar developed on GCC
    [TamaCollar1_Mk1_(V45).brd, TamaCollar1_Mk1_(V45).sch, TamaCollar1_Mk1_PCB_v38 (V45).brd, TamaCollar1_Mk1_Schematic_v34 (V45).sch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]
2021-12-27 adds changes to make release and GPS work
    [TamaCollar1_Mk1_(V45).brd, TamaCollar1_Mk1_(V45).sch]
2021-12-29 Updating documentation for LBS, TC
    Updated documentation, production files, and reorganized files in general.
    From henceforth the git repo will be used for maintaining fabrication details, and the g.drive for internal documents.
    [LBS Mk1 PBS.xlsx, LBS1.2 Rev1.2 BOM.xlsx, LT1 Rev1 BOM.xlsx, MC1.1 Mk1 PBS.xlsx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]
2021-12-31 Updated TC and LBS hardware files
    Added TC hardware assembly notes
    Updated hardware TC1 to TC1.1A
    Updated hardware LBS1 to LBS1.2 (pending minor alignment revision)
    [Acrylic 2mm Window.dxf, Acrylic 5mm Button Cover.dxf, Acrylic 5mm Ports Cover.dxf, Acrylic 6mm Backplate.dxf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]
2022-01-01 Added MC1 & MC1.1
    I've added MC1 and MC1.1 as two similar but distinct collars, along with their own documentation.
    MC1.1 is still WIP at the moment.
    [MC1 Mk1 PBS(Degradable Release).xlsx, MC1.1 Mk1 PBS.xlsx, MediumCollar1 Case C Lid.stl, MediumCollar1 Case C.stl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]
2022-01-03 Improved changelog and removed erroneous component
    LBS1.2 C6 had a old entry, removed now.
    [LBS1.2 Rev1.2 BOM.xlsx]
2022-01-10 changes to make voltage reading work
2022-01-10 LBS
    Fixed error in LBS BOM
    BOM and PBS for TGM are WIP.
    [LBS1.2 Rev1.2 BOM.xlsx, TGM Mk1 PBS.xlsx, TGM Rev1 BOM.xlsx]
2022-01-10 Updated MC and LBS
    LBS1.2 to 1.3
    MC1.1 to 1.2
    Added 470R resistors to mosfets to limit inrush
    [LBS1.2 Rev1.2 BOM.xlsx, MC1.1 Rev1 BOM.xlsx, TGM Mk1 PBS.xlsx, TGM Rev1 BOM.xlsx]
2022-01-11 Processed TGM files
    TGM files are ready for production now.
    [TGM Rev1 BOM.xlsx]
2022-01-27 Added TGM Production files
    Added fab files for TGM's case, and updating MC1.1's PBS. TGM PBS is WIP.
    [3x General Clamp.stl, Cam Cap.stl, Cam Case Gasket PProf.dxf, Cam Case.stl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]
2022-01-28 MC1.1 & TGM tweaks
    Tweaked MC1.1 to improve prints
    TGM PBS updated,
    [Case C Lid.stl, Case C1.1.stl, LBS Mk1 PBS.xlsx, Latch.stl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]
2022-01-28 Update TGM Mk1 PBS.xlsx
    [TGM Mk1 PBS.xlsx]
2022-03-29 Updated MC1.1 PCB Rev1.2
    - Added Inrush resistors R8 & R9
    [TGM Mk1 PBS.xlsx]
2022-04-05 adds EEPROM and packet based config for RTC device ID and schedule
2022-04-25 with default schedule if no schedule set. Ignore the printing it's bit weird right now due to RAM optimization thing
2022-04-25 some fixes in printing
2022-04-25 automate the changing of device code during compile
2022-08-17 Expanded collar enclosures
    Added updated enclosures used during 2022 trials.
    [Hoisting Loops (Bolted).3mf, Loadcell Holder.3mf, MC1 Type D Backpack Lid.3mf, MC1 Type D Backpack Strap Loops.3mf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]
2022-10-04 splits the tama collar and medium collar formware and adds packet queing mechanism to the medium collar
    [stepper-board-current-testing.xlsx]
2023-02-20 Shifted firmware folders
    I've shifted the tamacollar_firmware & mediumcollar_firmware to their *device*/software folders to keep things organized.
    [stepper-board-current-testing.xlsx]
